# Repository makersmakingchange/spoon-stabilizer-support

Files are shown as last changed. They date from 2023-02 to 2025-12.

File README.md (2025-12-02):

# Spoon Stablizer Support
The Spoon Stabilizer Support is an adapted utensil for people who have difficulties with tremors when eating. It used both passive stabilization and weights to dampen the effect of hand tremors and make it easier to eat.

This device may help people with hand tremors or fine motor challenges due to essential tremors, Parkinson's disease, cerebral palsy, multiple sclerosis, muscular dystrophy, arthritis, stroke, Huntington's diesase, or spinal cord injury.

The design consists of metal cutlery that is cut to length and mounted into a 3D printable handle with some off-the-shelf hardware.

The design was created by [Ian Faulkner](https://www.printables.com/social/380579-ian-faulkner/about). Supporting documentation was created by [Neil Squire Society](https://www.neilsquire.ca/) / [Makers Making Change](https://www.makersmakingchange.com/).

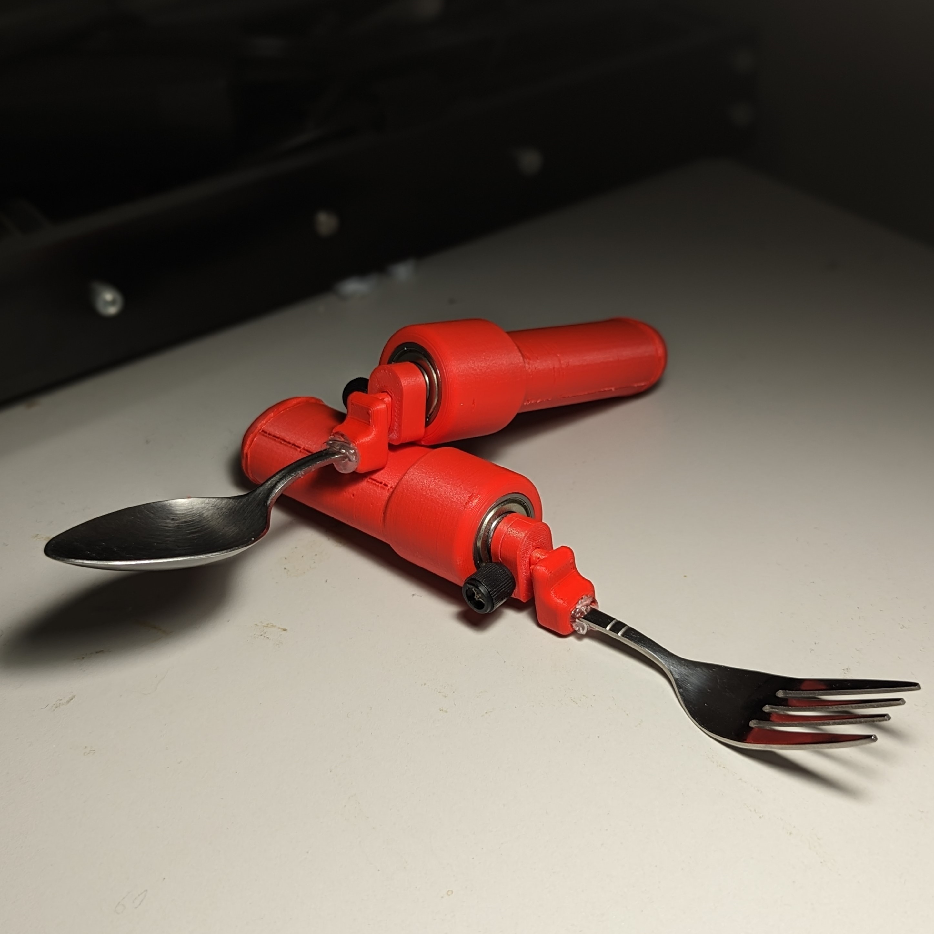
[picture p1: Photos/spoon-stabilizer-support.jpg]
Picture of Spoon Stabilizer Support.


Makers Making Change Assistive Device Library Listing: [https://www.makersmakingchange.com/s/product/spoon-stabilizer-support](https://www.makersmakingchange.com/s/product/spoon-stabilizer-support/01tJR0000009Sd0YAE)

## How to Obtain a Spoon Stablizer Support
### 1. Do it Yourself (DIY) or Do it Together (DIT)

This is an open-source assistive technology, so anyone is free to build it. All of the files and instructions required to build the Spoon Stablizer Support are contained within this repository. Refer to the Maker Checklist below.

### 2. Request a build of this device

If you would like to obtain a Spoon Stablizer Support, you may submit a build request through the [MMC Device Library Page](https://www.makersmakingchange.com/s/product/spoon-stabilizer-support/01tJR0000009Sd0YAE). The requestor is responsible for the cost of materials and any shipping.

### 3. How to build this device for someone else

If you have the skills and equipment to build this device, and would like to donate your time to create the switch for someone who needs it, visit the [MMC Maker Wanted](https://makersmakingchange.com/maker-wanted/) section.

## Getting Started

### 1. Read the Makers Checklist

The Makers Checklist contains the relevant steps to help build the device.

### 2. Order the Off-The-Shelf Components

The [Bill of Materials](/Documentation/Spoon_Stabilizer_Support_BOM.xlsx) lists all of the parts and components required to build the Spoon Stablizer Support.

### 3. Print the 3D Printable components

All of the files and individual print files can be in the [/Build_Files/3D_Printing_Files](/Build_Files/3D_Printing_Files/) folder.

### 4. Assemble the Spoon Stablizer Support

Reference the [Assembly Guide](/Documentation/Spoon_Stabilizer_Support_Assembly_Guide.pdf) for the tools and steps required to build each portion.

## Files
### Documentation
| Document             | Version | Link |
|----------------------|---------|------|
| Design Rationale     | 1.0     | [Spoon_Stabilizer_Support_Design_Rationale](/Documentation/Spoon_Stabilizer_Support_Design_Rationale.pdf)     |
| Maker Checklist      | 1.0     | [Spoon_Stabilizer_Support_Maker_Checklist](/Documentation/Spoon_Stabilizer_Support_Maker_Checklist.pdf)     |
| Bill of Materials    | 1.0     | [Spoon_Stabilizer_Support_Bill_of_Materials](/Documentation/Spoon_Stabilizer_Support_BOM.csv)     |
| 3D Printing Guide    | 1.0     | [Spoon_Stabilizer_Support_3D_Printing_Guide](/Documentation/Spoon_Stabilizer_Support_3D_Printing_Guide.pdf)     |
| Assembly Guide       | 1.0     | [Spoon_Stabilizer_Support_Assembly_Guide](/Documentation/Spoon_Stabilizer_Support_Assembly_Guide.pdf)     |
| User Guide           | 1.0     | [Spoon_Stabilizer_Support_User_Guide](/Documentation/Spoon_Stabilizer_Support_User_Guide.pdf)    |
| Changelog            | 1.0     | [Spoon_Stabilizer_Support_Changelog](/Documentation/Spoon_Stabilizer_Support_Changelog.pdf)     |

### Design Files
 - [CAD Files](/Design_Files/CAD_Design_Files/)

### Build Files
 - [3D Printing Files](/Build_Files/3D_Printing_Files)

## Attribution
 - The [Spoon/Fork Stabilizer](https://www.makersmakingchange.com/s/product/spoon-stabilizer-support/01tJR0000009Sd0YAE) was designed by [Ian Faulkner](https://www.printables.com/social/380579-ian-faulkner/about) and made available under a [Creative Commons Attribution-NonCommercial 4.0 ](https://creativecommons.org/licenses/by-nc/4.0/) license.
 - Documentation was created by Neil Squire Society/Makers Making Change.

## License
The Spoon Stablizer Support design is licensed under [Creative Commons Attribution-NonCommercial 4.0 ](https://creativecommons.org/licenses/by-nc/4.0/)

Accompanying material such as instruction manuals, videos, and other copyrightable works that are useful but not necessary to design, make, test, or prepare the Spoon Stablizer Support are published under a Creative Commons Attribution-ShareAlike 4.0 license https://creativecommons.org/licenses/by-sa/4.0/ (CC BY-SA 4.0).

---

<!-- ABOUT MMC START -->
## About Makers Making Change
[Makers Making Change Logo](https://www.makersmakingchange.com/)

Makers Making Change is a program of [Neil Squire](https://www.neilsquire.ca/), a Canadian non-profit that uses technology, knowledge, and passion to empower people with disabilities.

Makers Making Change leverages the capacity of community based Makers, Disability Professionals and Volunteers to develop and deliver affordable Open Source Assistive Technologies.

 - Website: [www.MakersMakingChange.com](https://www.makersmakingchange.com/)
 - GitHub: [makersmakingchange](https://github.com/makersmakingchange)
 - Bluesky: [@makersmakingchange.bsky.social](https://bsky.app/profile/makersmakingchange.bsky.social)
 - Instagram: [@makersmakingchange](https://www.instagram.com/makersmakingchange)
 - Facebook: [makersmakechange](https://www.facebook.com/makersmakechange)
 - LinkedIn: [Neil Squire Society](https://www.linkedin.com/company/neil-squire-society/)
 - Thingiverse: [makersmakingchange](https://www.thingiverse.com/makersmakingchange/about)
 - Printables: [MakersMakingChange](https://www.printables.com/@MakersMakingChange)

### Contact Us
For technical questions, to get involved, or to share your experience we encourage you to [visit our website](https://www.makersmakingchange.com/) or [contact us](https://www.makersmakingchange.com/s/contact).
<!-- ABOUT MMC END -->

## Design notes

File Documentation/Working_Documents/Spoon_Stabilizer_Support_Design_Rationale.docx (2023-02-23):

# Introduction

A device for those who have difficulties with tremors when eating. It used both passive stabilization and weights to dampen the effect of hand tremors.

# Research

Below is a table of existing commercial or DIY options that are similar.

Name | Picture | Price | Link

Commercial

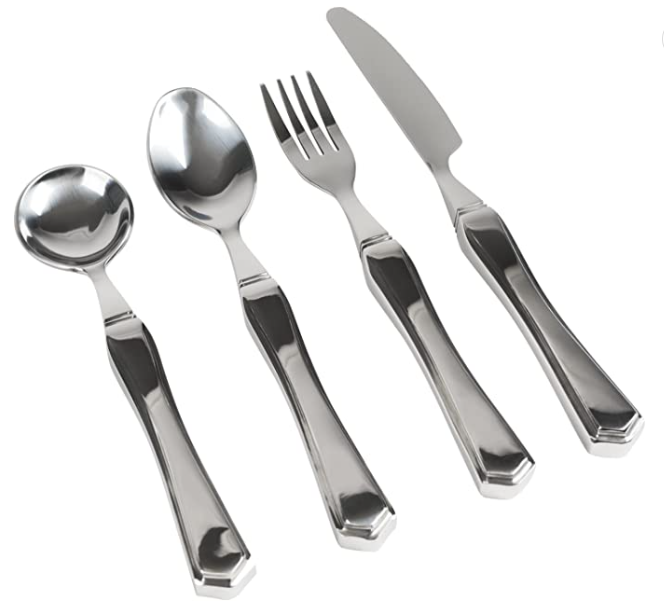
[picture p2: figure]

Vive Weighted Utensils | | $55.46 | Link (https://www.amazon.ca/Vive-7oz-Weighted-Utensils-Piece/dp/B075Y3N1MZ)

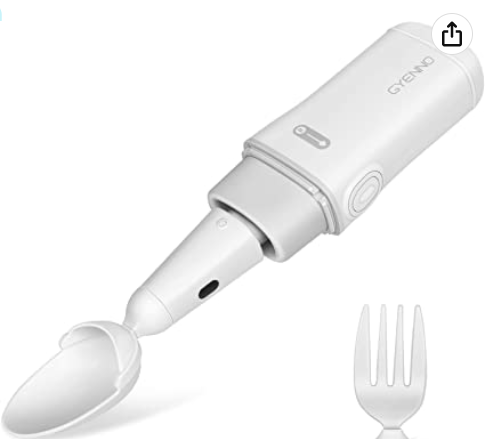
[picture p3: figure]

GYENNO Bravo Twist | | $399 | Link (https://www.amazon.ca/GYENNO-Twist-Parkinson-Stabilizing-Parkinsons/dp/B07FRPX2H8?hvadid=353068188462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)

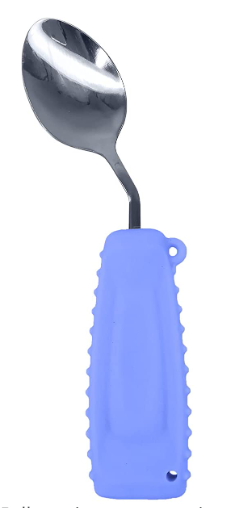
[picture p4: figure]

Ehucon Adaptive Utensils | | $22.32 | Link (https://www.amazon.ca/Ehucon-Untensils-Parkinsons-Lightweight-Ergonomic/dp/B09QGBSPK9?hvadid=353068188462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)

DIY

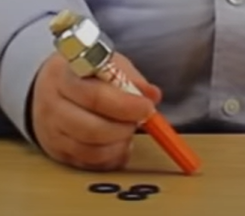
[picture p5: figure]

DIY Weighted Marker | | N/A | Link (https://www.youtube.com/watch?v=PVcX0uTqMMg)

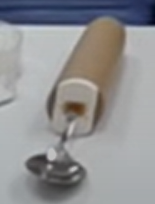
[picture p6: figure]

DIY Weighted Fork | | N/A | Link (https://ohanaot.com/make-weighted-pencil-fork-spoon-kids-autism/)

# Requirements

## Goals

G01 | Create a weighted utensil that stabilizes the tremors of a user’s hand

## Functional Requirements

F01 | Device must be weighted
F02 | Device must have passive spill prevention
F03 | Device must be cleanable

## Non-functional Requirement

NF01 | Device must be made from off the shelf components and 3D printed parts

## Constraints

C01 | Device must cost less than 10 dollars

# Testing

After assembling the device, it was tested to see if it would fail. It was found that 20% infill was too weak for some parts, so they were changed to 100% infill for added strength.

# Opportunities for Improvement

The device could be printed in ABS or another dishwasher safe material.

Printability improvements could be made to reduce support use.

© 2023 by Neil Squire. This work is licensed under the CC BY SA 4.0 License: http://creativecommons.org/licenses/by-sa/4.0 Files available at https://makersmakingchange.com/project/spoon-stabilizer-support/ Page 2 of 3

V1.0 | February 2023 Spoon Stabilizer Support Design Rationale

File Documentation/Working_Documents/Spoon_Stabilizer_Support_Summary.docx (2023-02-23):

# Title

Spoon Stabilizer Support

## Subtitle

A device for those who have difficulties with tremors when eating. The Spoon Stabilizer Support uses both passive stabilization and weights to dampen the effect of hand tremors.

## Device Details

### Overview

A device for those who have difficulties with tremors when eating. It used both passive stabilization and weights to dampen the effect of hand tremors.

### Usage

Attach either the spoon or fork attachment to the handle using the set screw. The device can then be used as a normal spoon or fork.

### Cost

<$5

### Build Instructions

After all supports are removed, superglue the bearing into the handle, and the insert into the bearing. Cut the spoon near the head, and glue it into the spoon attachment. Connect the spoon attachment to the insert using the computer case screws. If the user wants a weighted handle, insert the fishing weights into the handle. Finally, glue the grip insert onto the end of the handle.

#### Skills Required

- 3D Printing

#### Time Required

3D Printing Time: 308 min

Assembly Time: 10 min

#### Tools

- 3D Printer
- Tin Snips
- Superglue
- Hot Glue

#### Components

- Bearings
- Computer Case Screws
- Fishing Weights
- Utensil

#### 3D Printing

- Grip Handle
- Grip Insert
- Insert
- Spoon attachment

### Attribution

Design by Ian Faulkner (https://www.printables.com/social/380579-ian-faulkner/about)

Documentation by Neil Squire Society/Makers Making Change

© 2023 by Neil Squire. This work is licensed under the CC BY SA 4.0 License: http://creativecommons.org/licenses/by-sa/4.0 Files available at https://makersmakingchange.com/project/spoon-stabilizer-support/ Page 2 of 3

V1.0 | February 2023 Spoon Stabilizer Support Summary

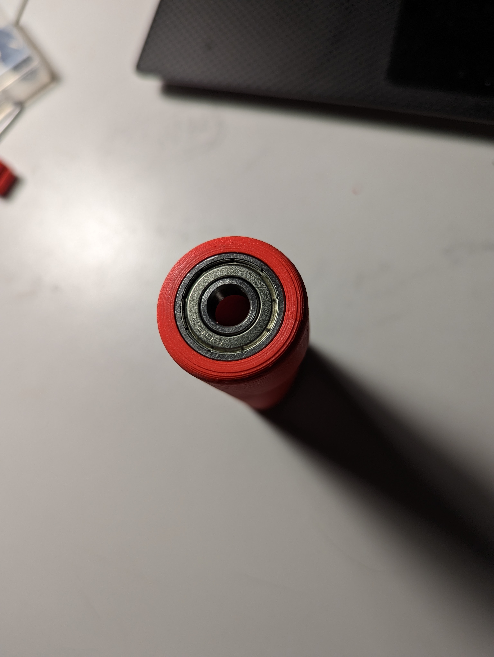
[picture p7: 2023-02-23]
Photos/bearing inserted.jpg

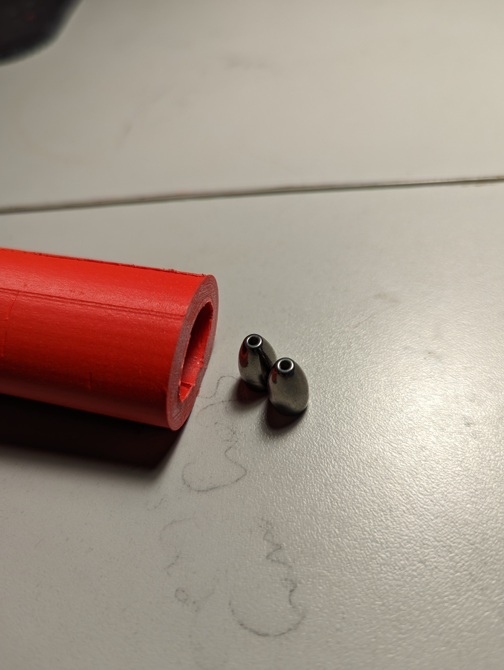
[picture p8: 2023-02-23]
Photos/weights.jpg

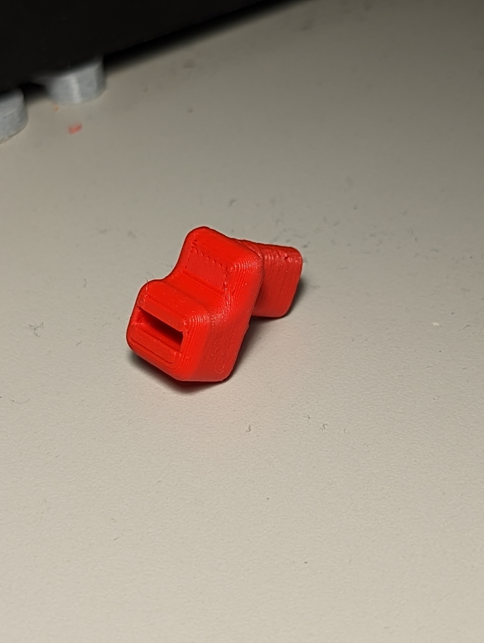
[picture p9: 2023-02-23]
Photos/spoon attachment.jpg

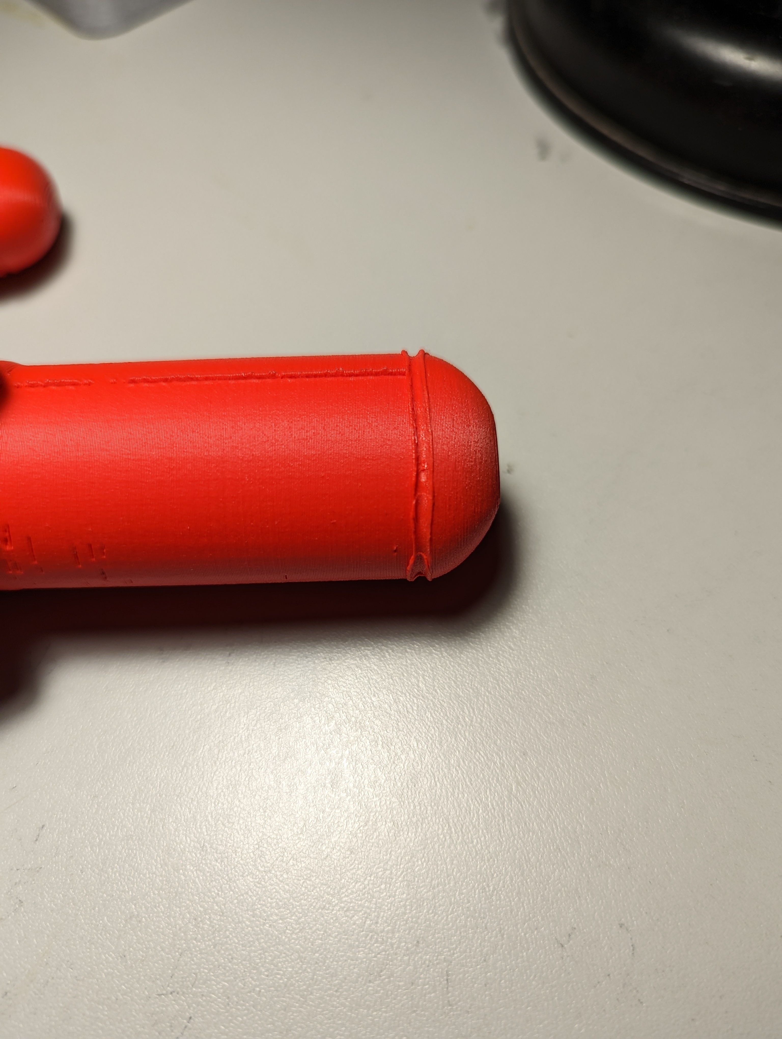
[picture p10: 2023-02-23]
Photos/handle endcap.jpg

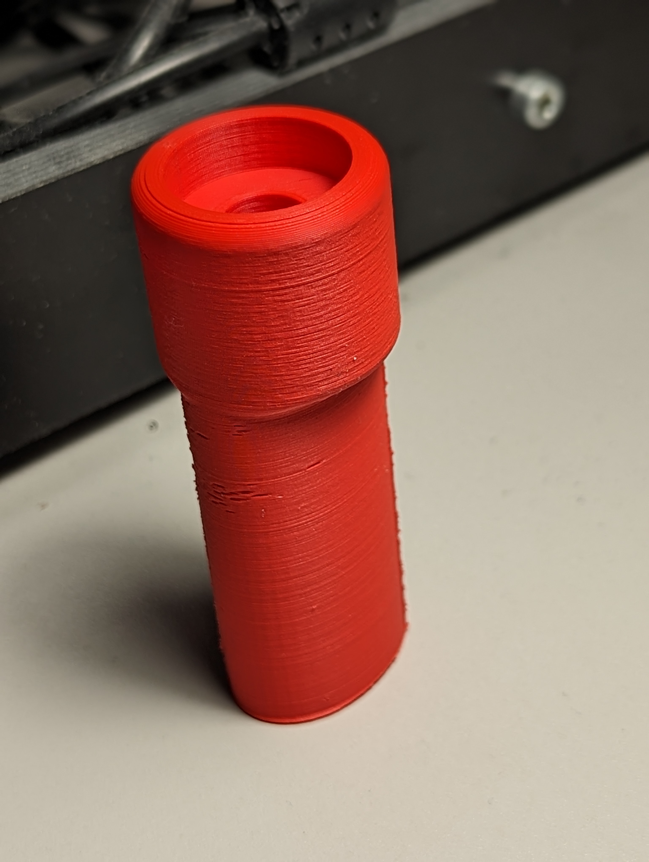
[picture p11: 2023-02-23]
Photos/handle grip.jpg

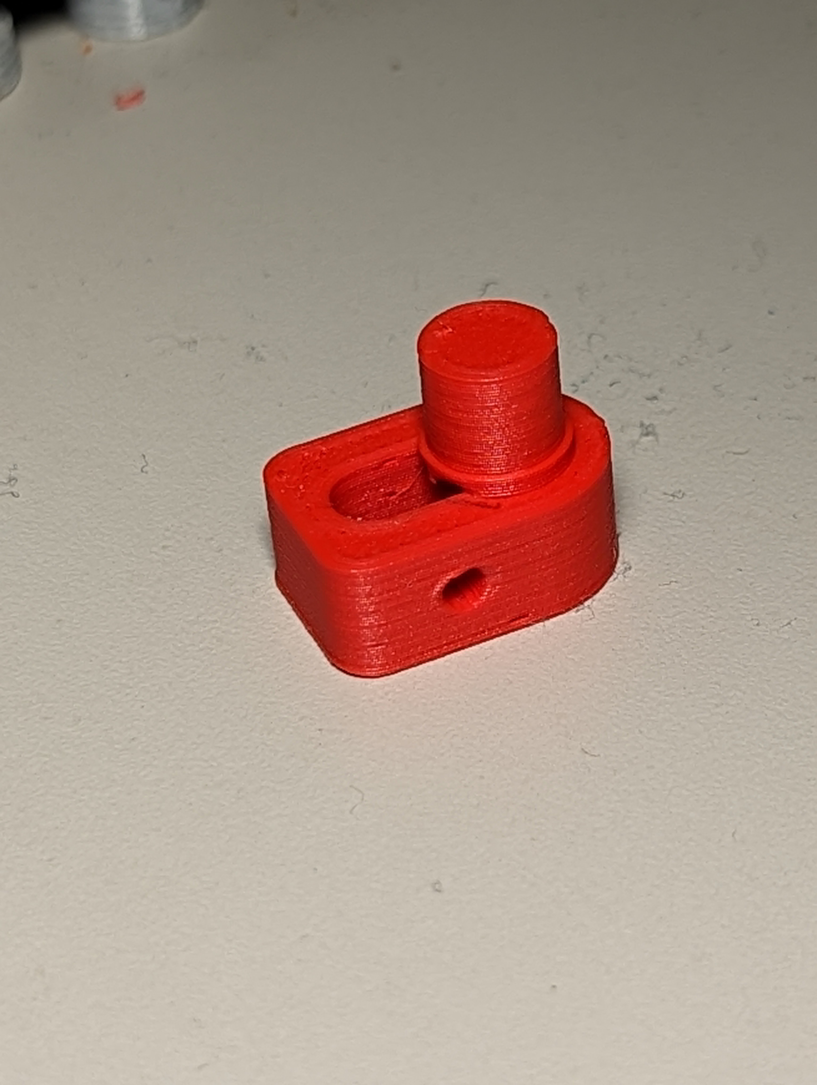
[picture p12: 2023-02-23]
Photos/insert.jpg

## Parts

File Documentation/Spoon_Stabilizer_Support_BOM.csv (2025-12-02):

Device: Spoon Stabilizer Support |  | Total Cost | Total Print time (hr) | Total filament (g) | Unit Cost
Version: V1.0 | Last Updated: 2025-Dec-02 | $50.43 | 4.97 | 33 | $5.55
Commercial Parts
Part type (Electrical, Mechanical, Sanitization, etc) | Part Name | Quantity Needed | Pkg Quantity | Price per package | Price per Unit | Price for qty needed | Link
Mechanical | Bearing, 608-ZZ | 1 | 10 | $11.55 | $1.16 | $1.16 | https://www.amazon.ca/gp/product/B07XLV1W2M
Mechanical | Computer Case Screws | 1 | 10 | $9.89 | $0.99 | $0.99 | https://www.amazon.ca/gp/product/B07TXS98L6
Mechanical | Fishing Weights | 2 | 10 | $13.99 | $1.40 | $2.80 | https://www.amazon.ca/gp/product/B0B1JBJ91F
Mechanical | Spoon | 1 | 12 | $14.17 | $1.18 | $1.18 | https://www.amazon.ca/Winco-0005-03-12-Piece-Dinner-Stainless/dp/B004UNF2II
3D Printed Parts ESTIMATED PRICING USING 1KG ROLL COST: | $25.00
Part | Description | Quantity Needed | TOTAL Mass (g) | Estimated Price | Print Time (Min) | Link
Grip Handle | Main Handle | 1 | 26 | $0.65 | 224
Grip Insert | Handle endcap | 1 | 2 | $0.05 | 15
Insert | Connects spoon to bearing | 1 | 2 | $0.05 | 27
Spoon attachment | Connects to spoon | 1 | 3 | $0.08 | 32
 |  |  |  | $-
 |  |  | Total Print Cost: | $0.83
Tools for Assembly
Alternatives (if there are other sources for some parts link them below)
Part and description | Link

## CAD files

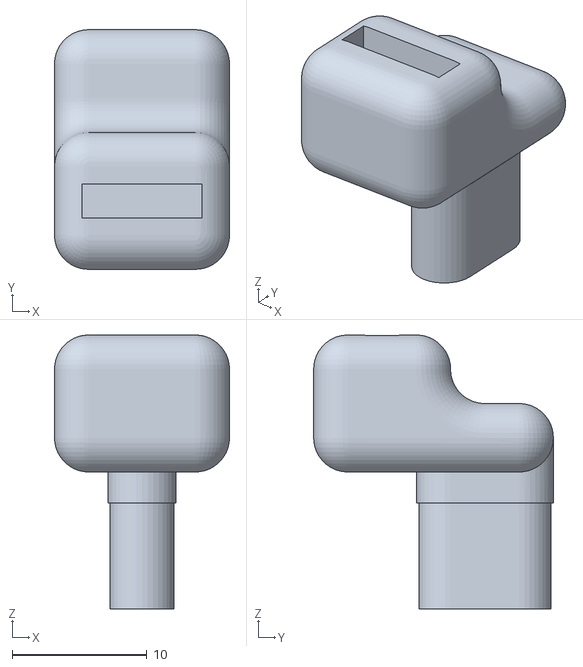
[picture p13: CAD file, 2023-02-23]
Build_Files/3D_Printing_Files/spoon attatchment.STL
13.0 x 17.8 x 20.3

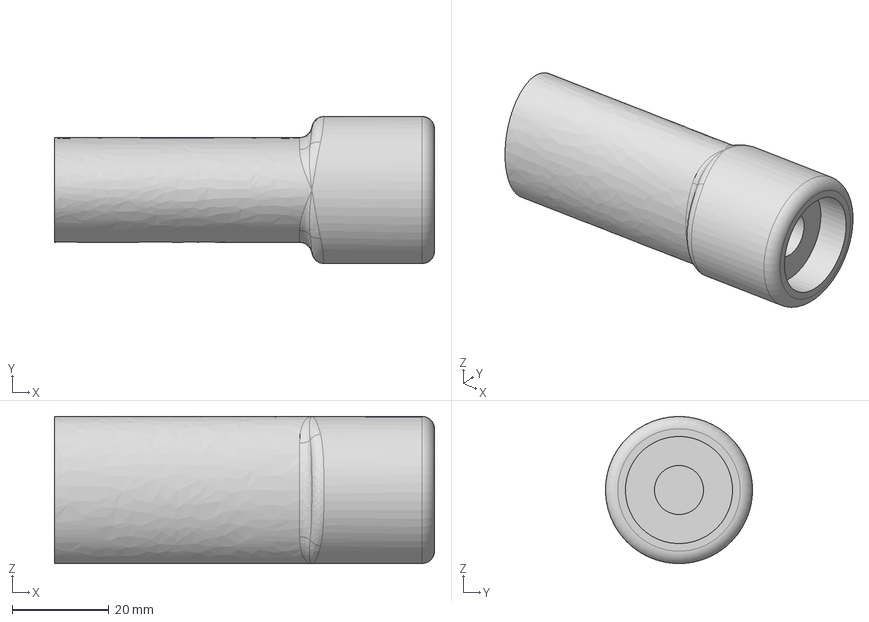
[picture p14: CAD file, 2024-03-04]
Design_Files/CAD_Design_Files/Grip Handle.step
78.7 x 30.5 x 30.5 mm

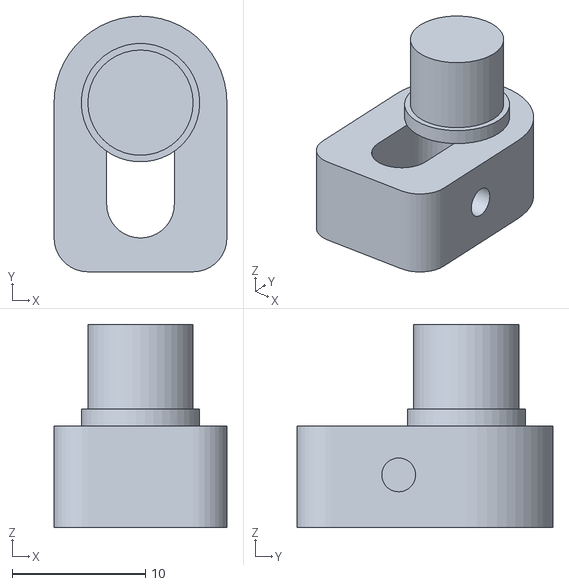
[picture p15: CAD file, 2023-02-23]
Build_Files/3D_Printing_Files/insert.STL
13.0 x 19.2 x 15.2

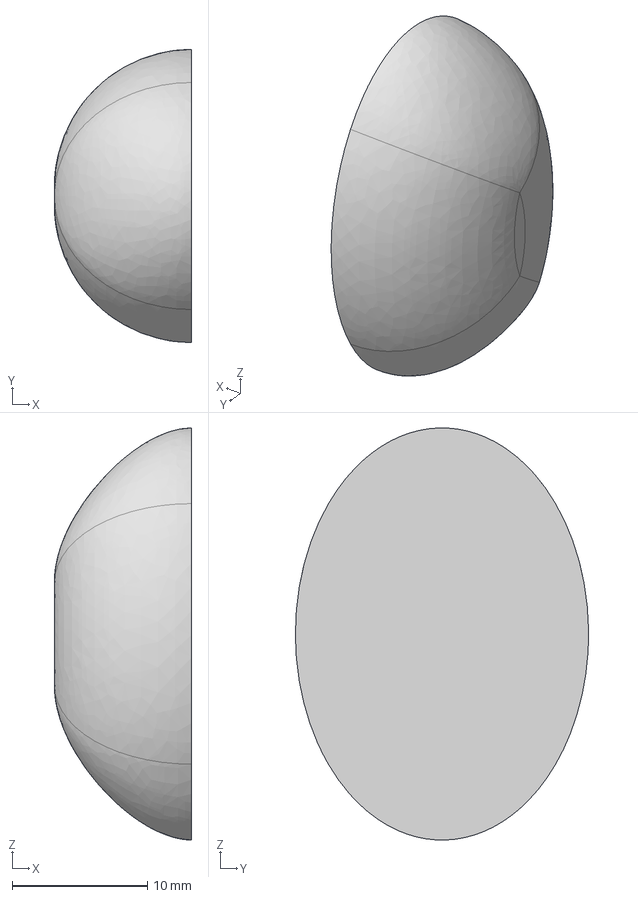
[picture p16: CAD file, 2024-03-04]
Design_Files/CAD_Design_Files/Grip.step
10.2 x 21.7 x 30.5 mm

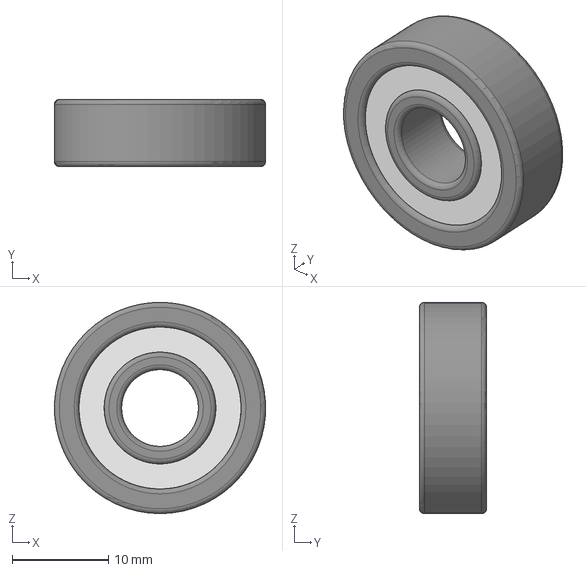
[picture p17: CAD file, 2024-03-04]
Design_Files/CAD_Design_Files/bearing.step
22.0 x 7.00 x 22.0 mm

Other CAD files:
Build_Files/3D_Printing_Files/Grip Handle.STL
Design_Files/CAD_Design_Files/insert.step
Build_Files/3D_Printing_Files/Grip Insert.stl
Design_Files/CAD_Design_Files/spoon attatchment.step
Design_Files/CAD_Design_Files/Grip Handle.SLDPRT
Design_Files/CAD_Design_Files/Grip Handle.f3d
Design_Files/CAD_Design_Files/Grip.SLDPRT
Design_Files/CAD_Design_Files/Grip.f3d
Design_Files/CAD_Design_Files/bearing.SLDPRT
Design_Files/CAD_Design_Files/bearing.f3d
Design_Files/CAD_Design_Files/insert.SLDPRT
Design_Files/CAD_Design_Files/insert.f3d
Design_Files/CAD_Design_Files/spoon attatchment.SLDPRT
Design_Files/CAD_Design_Files/spoon attatchment.f3d

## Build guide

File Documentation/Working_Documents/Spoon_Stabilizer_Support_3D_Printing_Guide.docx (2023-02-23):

# 3D Printing Summary

Metrics
Total Print Time (min) | 308
Total Number of Components | 4
Typical Total Mass (g) | 33
Typical Number of Print Setups | 4

# 3D Printing Settings

Print File Name | Qty | Total Print Time (hr:min) | Mass (g) | Infill (%) | Support(Y/N) | Layer Height/ Nozzle Diameter(mm) | Notes (orientation, special settings, etc.)
Grip Handle.stl | 1 | 3:44 | 26 | 20 | Y | 0.2/0.4 | - Requires support - Print in orientation given in STL
Grip Insert.stl | 1 | 0:15 | 2 | 20 | N | 0.2/0.4 | - Print in orientation given in STL
insert.stl | 1 | 0:27 | 2 | 20 | Y | 0.2/0.4 | - Requires support - Print in orientation given in STL
spoon attachment.stl | 1 | 0:32 | 3 | 20 | Y | 0.2/0.4 | - Requires support - Print in orientation given in STL

# Customization Options

- The device can be printed in any colour the user would like.

# Post-Processing

- Remove support material
- Remove any sharp edges using a hobby knife or sandpaper

# Examples of Quality Prints

Photos of Grip Handle.stl

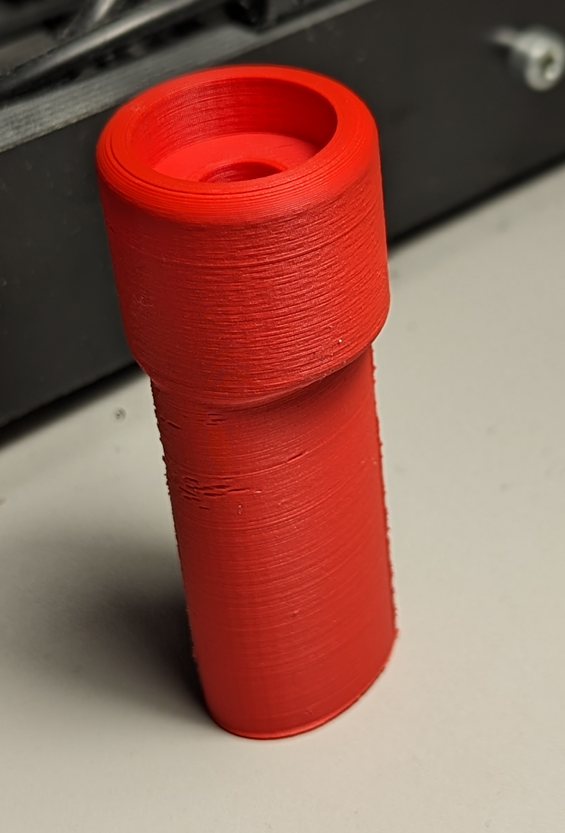
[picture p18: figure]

Photos of Grip Insert.stl

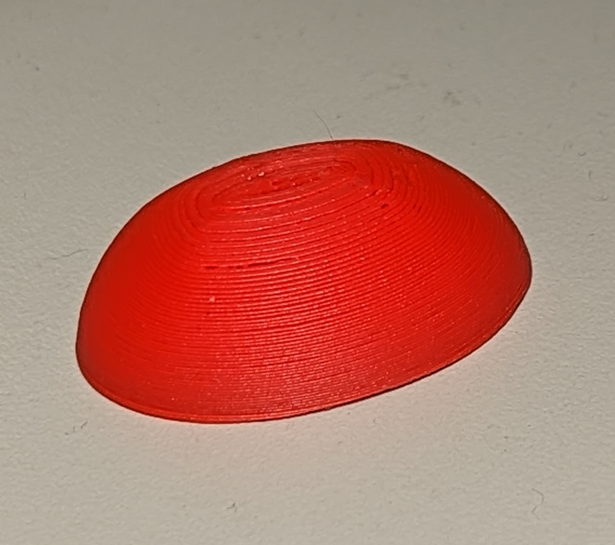
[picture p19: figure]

Photos of insert.stl

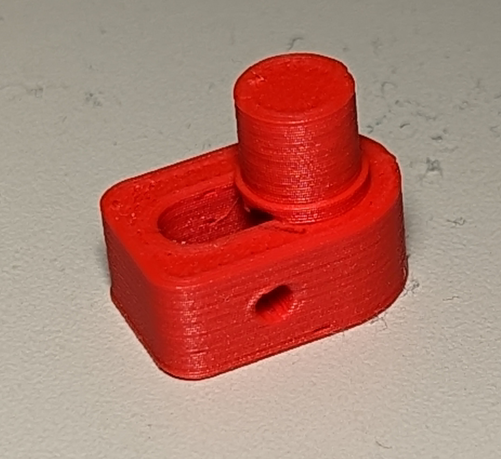
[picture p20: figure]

Photos of spoon attachment.stl

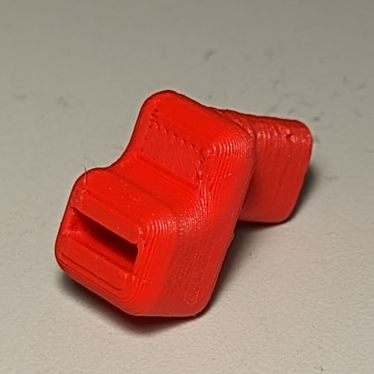
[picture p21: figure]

© 2023 by Neil Squire. This work is licensed under the CC BY SA 4.0 License: http://creativecommons.org/licenses/by-sa/4.0 Files available at https://makersmakingchange.com/project/spoon-stabilizer-support/ Page 1 of 2

V1.0 | February 2023 Spoon Stabilizer Support 3D Printing Guide

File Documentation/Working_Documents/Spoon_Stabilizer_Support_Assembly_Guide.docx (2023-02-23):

# Required Components

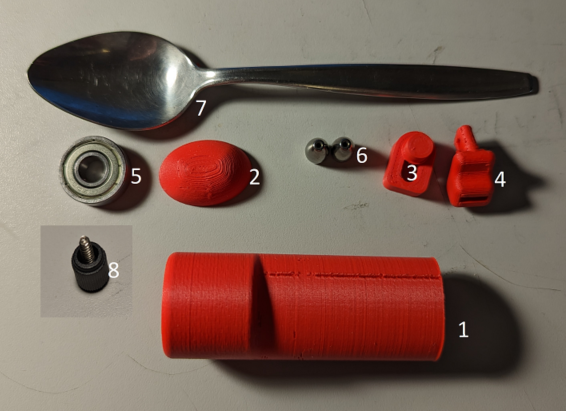
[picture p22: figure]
All components of the device, laid out and numbered.

| BOM 1. Grip Handle 2. Grip insert 3. Insert 4. Spoon attachment 5. Bearing 6. Fishing weights 7. Utensil 8. Computer case screw

# Required Tools

- Tin Snips
- Superglue
- Hot Glue

# Required Personal Protective Equipment (PPE)

- Eye protection

# Assembly Instructions

## Step 1

Use superglue to glue the bearing into the grip handle. Be careful to not get any into the bearing.

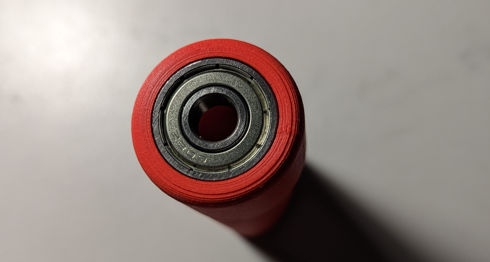
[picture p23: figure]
The handle of the device with the bearing glued in place.

## Step 2

Use superglue to attach the insert into the bearing. Be careful not to get any into the bearing.

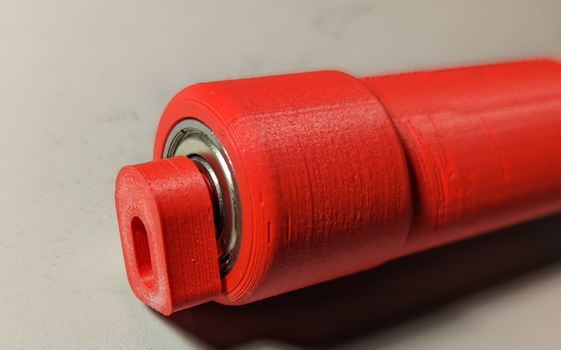
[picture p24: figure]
The handle and bearing with the insert glued into the centre of the bearing.

## Step 3

Cut the utensil at the desired length and hot glue it into the slot on the spoon attachment.

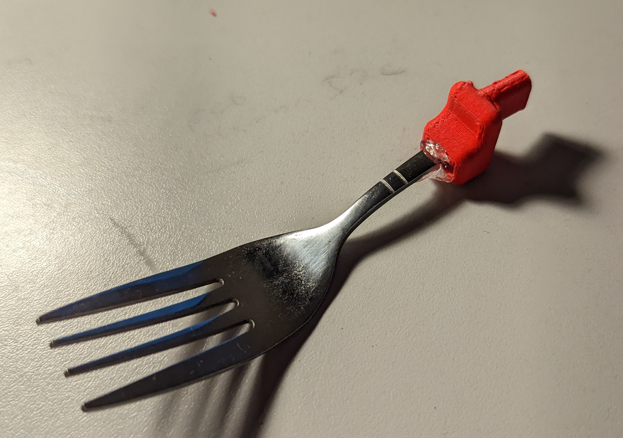
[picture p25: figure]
The utensil attachment with a fork cut to length and glued in place.

## Step 4

Using the set screw, attach the spoon section to the handle section.

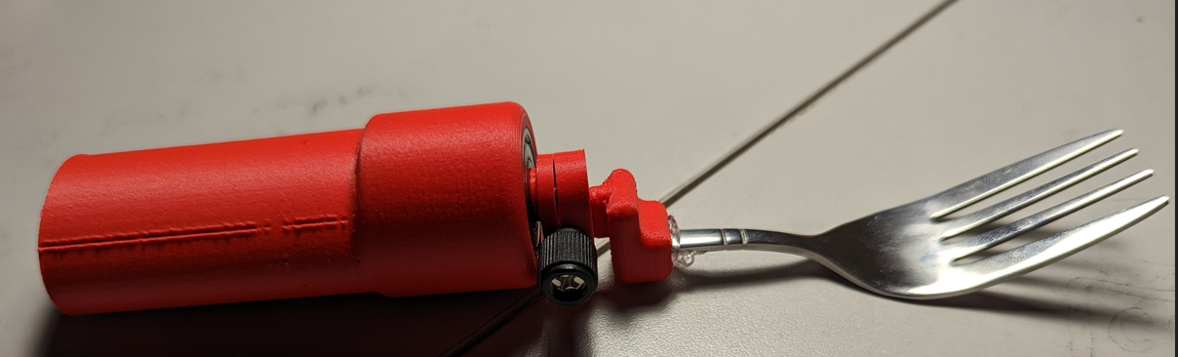
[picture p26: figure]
The utensil attachment attached to the handle assembly.

## Step 5

If the user wants a weighted utensil, add the desired amount of weights to the hollow handle section. A tissue can optionally be used to prevent the weights from sliding around in the handle.

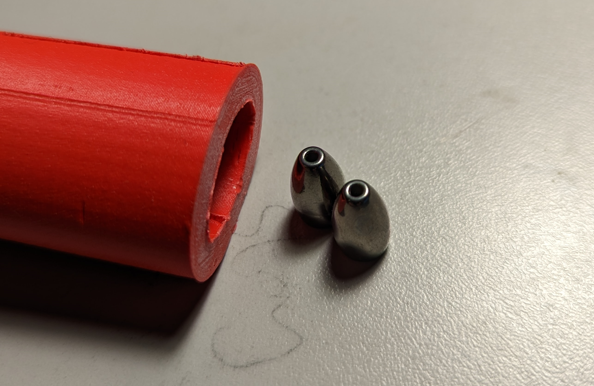
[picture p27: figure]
Two weights next to the hollow device handle.

## Step 6

Use superglue to attach the grip insert to the end of the handle. Optionally, a soldering iron can be used to melt the two pieces together.

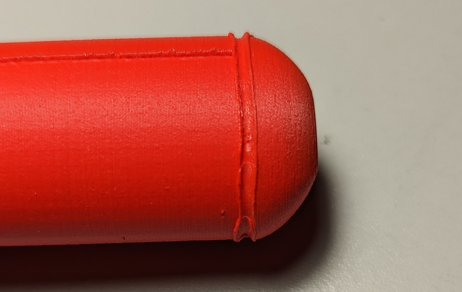
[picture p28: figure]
The handle with the endcap attached.

© 2023 by Neil Squire. This work is licensed under the CC BY SA 4.0 License: http://creativecommons.org/licenses/by-sa/4.0 Files available at https://makersmakingchange.com/project/spoon-stabilizer-support/ Page 2 of 3

V1.0 | February 2023 Spoon Stabilizer Support Assembly Guide

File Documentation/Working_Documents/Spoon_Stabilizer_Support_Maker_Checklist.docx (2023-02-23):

# Maker To Do List

- Read through the Assembly Guide to become familiar with required components, tools, supplies, and safety gear and overall assembly steps.
- Talk to User about customization options (e.g., color, any special requests, etc.)
- Order hardware components
- Gather tools, supplies, and safety equipment.
- Assemble the device
- Test device
- Print “User Quick Guide”

# Items to Give to User

- Assembled, tested device
- “User Quick Guide”

© 2023 by Neil Squire. This work is licensed under the CC BY SA 4.0 License: http://creativecommons.org/licenses/by-sa/4.0 Files available at https://makersmakingchange.com/project/spoon-stabilizer-support/ Page 2 of 3

V1.0 | February 2023 Spoon Stabilizer Support Maker Checklist

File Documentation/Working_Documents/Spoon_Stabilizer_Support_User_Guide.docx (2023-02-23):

## Introduction

A device for those who have difficulties with tremors when eating. It uses both passive stabilization and weights to dampen the effect of hand tremors.

## Features

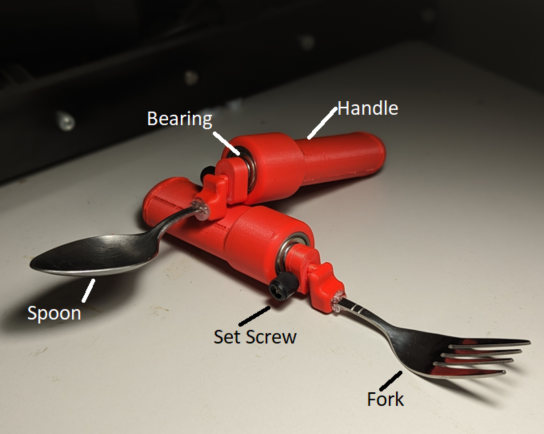
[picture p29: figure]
Labeled picture of two of the devices, one a spoon, and the other a fork

## Usage

Attach either the spoon or fork attachment to the handle using the set screw. The device can then be used as a normal spoon or fork.

## Compatibility

The device is compatible with any spoon or fork that has a cross section of 9x2.5mm or less.

## Specifications

Handle has a length of 90mm, and a diameter of 30mm. The entire device has a weight of 60 g.

## Cleaning

The device can be wiped clean with a damp cloth. The section with the fork/spoon can be detached for easier cleaning.

© 2023 by Neil Squire. This work is licensed under the CC BY SA 4.0 License: http://creativecommons.org/licenses/by-sa/4.0 Files available at https://makersmakingchange.com/project/spoon-stabilizer-support/ Page 1 of 2

V1.0 | February 2023 Spoon Stabilizer Support user Quick Guide

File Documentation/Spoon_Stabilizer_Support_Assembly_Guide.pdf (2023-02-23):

V1.0 | February 2023

# Spoon Stabilizer Support

# ASSEMBLY GUIDE

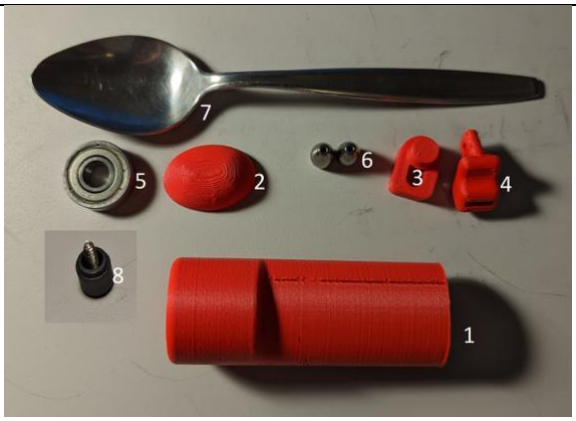
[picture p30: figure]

© 2023 by Neil Squire. (https://neilsquire.ca/)
This work is licensed under the CC BY SA 4.0 License: http://creativecommons.org/licenses/by-sa/4.0
Files available at https://makersmakingchange.com/project/spoon-stabilizer-support/ | Page 1 of 4

# Required Components

## BOM 1. Grip Handle 2. Grip insert 3. Insert 4. Spoon attachment 5. Bearing 6. Fishing weights 7. Utensil 8. Computer case screw

# Required Tools

## - Tin Snips - Superglue - Hot Glue

# Required Personal Protective Equipment (PPE)

## - Eye protection

# ASSEMBLY GUIDE

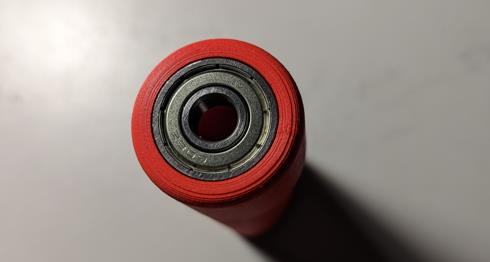
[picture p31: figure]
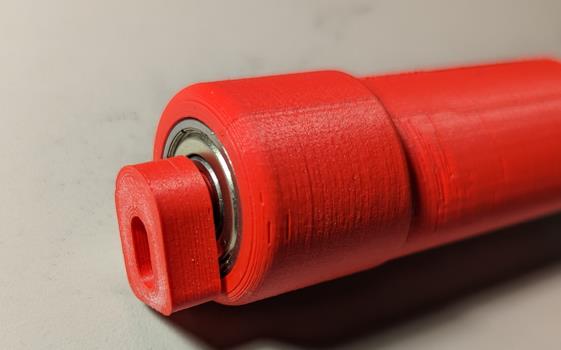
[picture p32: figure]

Files available at https://makersmakingchange.com/project/spoon-stabilizer-support/ | Page 2 of 4

# Assembly Instructions

## Step 1

Use superglue to glue the bearing into the grip handle. Be careful to not get any into the bearing.

## Step 2

Use superglue to attach the insert into the bearing. Be careful not to get any into the bearing.

# ASSEMBLY GUIDE

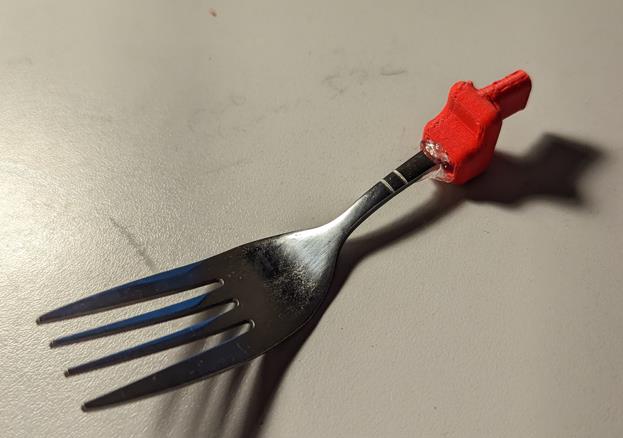
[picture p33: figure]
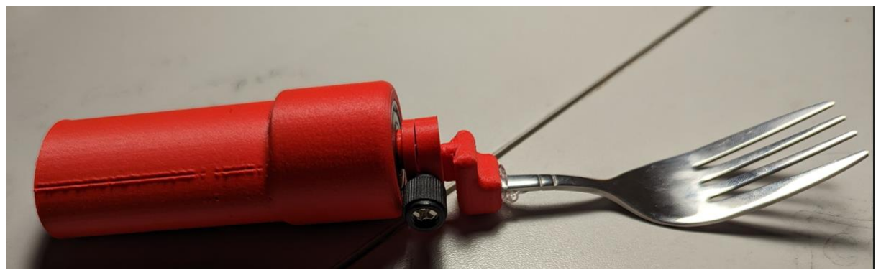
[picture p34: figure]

Files available at https://makersmakingchange.com/project/spoon-stabilizer-support/ | Page 3 of 4

## Step 3

Cut the utensil at the desired length and hot glue it into the slot on the spoon attachment.

## Step 4

Using the set screw, attach the spoon section to the handle section.

# ASSEMBLY GUIDE

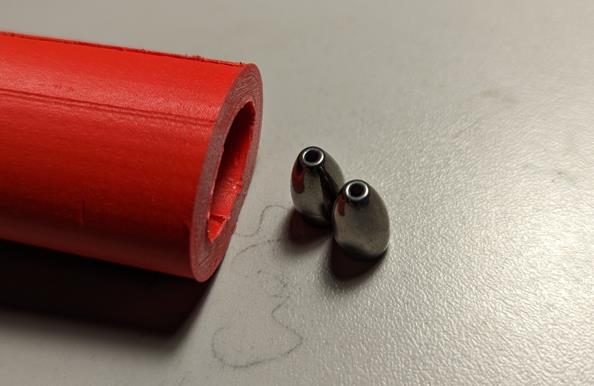
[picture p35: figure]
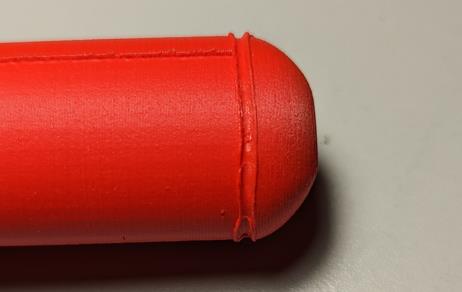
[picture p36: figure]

Files available at https://makersmakingchange.com/project/spoon-stabilizer-support/ | Page 4 of 4

## Step 5

If the user wants a weighted utensil, add the desired amount of weights to the hollow handle section. A tissue can optionally be used to prevent the weights from sliding around in the handle.

## Step 6

Use superglue to attach the grip insert to the end of the handle. Optionally, a soldering iron can be used to melt the two pieces together.

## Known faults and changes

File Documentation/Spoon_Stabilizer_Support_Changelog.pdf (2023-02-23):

V1.0 | February 2023

# Spoon Stabilizer Support

# CHANGELOG

© 2023 by Neil Squire. (https://neilsquire.ca/)
This work is licensed under the CC BY SA 4.0 License: http://creativecommons.org/licenses/by-sa/4.0
Files available at https://makersmakingchange.com/project/spoon-stabilizer-support/ | Page 1 of 1

# Version 1.0 | 2023/02/17

## - Design by Ian Faulkner (https://www.printables.com/social/380579-ian-faulkner/about) - Documentation by Neil Squire Society/Makers Making Change

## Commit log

2024-03-04 Add Autodesk Fusion and step versions of CAD files
    [Grip Handle.SLDPRT, Grip Handle.f3d, Grip Handle.step, Grip.SLDPRT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]
2024-03-04 Update documentation naming
    Remove versioning to simplify links
    [Spoon_Stabilizer_Support_BOM_.xlsx, Spoon_Stabilizer_Support_BOM_V1.0.xlsx]
2025-12-02 Update Spoon_Stabilizer_Support_BOM.xlsx
    Update total cost calculation. Simplify product links.
    [Spoon_Stabilizer_Support_BOM.xlsx]
